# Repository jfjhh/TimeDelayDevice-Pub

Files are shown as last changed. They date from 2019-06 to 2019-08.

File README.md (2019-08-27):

Time Delay Device Documentation
===============================

See `./doc/doc-all.pdf`. It's header is reproduced below.

All of the documentation concerning the auxilliary files for the project
is assembled here. What follows is a description of the contents of each
directory.

-   `adjustable-delay`: Schematics and ideas for implementing adjustable
    delay in the circuit. The subdirectory `Linear` contains a tenative
    schematic (KiCAD files and <span
    style="font-variant:small-caps;">pdf</span>) of a circuit that
    implements the different clock frequencies by counting, while
    `Arbitrary` gives what I have so far in creating an arbitrary delay
    circuit.

-   `arduino`: The code uploaded to the Arduino Due.

-   `characterization`: Contains many different parts of the code used
    to analyze the characterization data for the device, and includes
    instructions on how to program the history.

-   `doc`: The top-level documentation directory (this one).

-   `fifo-p3f`: The KiCAD files for the device, as well as a schematic
    <span style="font-variant:small-caps;">pdf</span> and the gerber
    files that I sent for manufacture.

-   `figures`: The images and GNUPlot code used to create the figures
    for the paper.[^1]

-   `program-rescaling`: The code used to calculate the gain and offset
    resistor values to be optimal, given the constraints of E-series
    values and the overall resistances needed.

-   `triangle`: The code used to generate the spumpus (initial history
    signal) for the triangle-<span
    style="font-variant:small-caps;">dde</span> (relay-control) circuit
    in the paper. This is a good starting point if you want to program
    something different.

[^1]: *Spumpus* stands for spiky lumpus, where *lumpus* refers to a
    lumpy-looking signal. We want a strange signal for the programming
    to demonstrate that it is really *arbitrary*.

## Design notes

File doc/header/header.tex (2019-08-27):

%        File: header.tex
%     Created: Mon Aug 26 08:00 PM 2019 P
% Last Change: Mon Aug 26 08:00 PM 2019 P
%
\documentclass[11pt,letterpaper]{article}

\title{Time Delay Device Files Documentation}
\author{Alex Striff}
\date{August 26, 2019}

\begin{document}
\maketitle

All of the documentation concerning the auxilliary files for the project is
assembled here. What follows is a description of the contents of each directory.

\begin{itemize}
  \item \texttt{adjustable-delay}: Schematics and ideas for implementing
    adjustable delay in the circuit. The subdirectory \texttt{Linear} contains a
    tenative schematic (KiCAD files and \textsc{pdf}) of a circuit that
    implements the different clock frequencies by counting, while
    \texttt{Arbitrary} gives what I have so far in creating an arbitrary delay
    circuit.
  \item \texttt{arduino}: The code uploaded to the Arduino Due.
  \item \texttt{characterization}: Contains many different parts of the
    code used to analyze the characterization data for the device, and includes
    instructions on how to program the history.
  \item \texttt{doc}: The top-level documentation directory (this one).
  \item \texttt{fifo-p3f}: The KiCAD files for the device, as well as a
    schematic \textsc{pdf} and the gerber files that I sent for manufacture.
  \item \texttt{figures}: The images and GNUPlot code used to create the figures
    for the paper.\footnote{\emph{Spumpus} stands for spiky lumpus, where
      \emph{lumpus} refers to a lumpy-looking signal. We want a strange signal
    for the programming to demonstrate that it is really \emph{arbitrary}.}
  \item \texttt{program-rescaling}: The code used to calculate the gain and
    offset resistor values to be optimal, given the constraints of E-series
    values and the overall resistances needed.
  \item \texttt{triangle}: The code used to generate the spumpus (initial
    history signal) for the triangle-\textsc{dde} (relay-control) circuit in the
    paper. This is a good starting point if you want to program something
    different.
\end{itemize}

\end{document}

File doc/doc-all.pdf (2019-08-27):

# Time Delay Device Files Documentation

Alex Striff

August 26, 2019

All of the documentation concerning the auxilliary files for the project is assembled here. What follows is a description of the contents of each directory.

- adjustable-delay: Schematics and ideas for implementing adjustable delay in the circuit. The subdirectory Linear contains a tenative schematic (KiCAD files and pdf) of a circuit that implements the different clock frequencies by counting, while Arbitrary gives what I have so far in creating an arbitrary delay circuit.
- arduino: The code uploaded to the Arduino Due.
- characterization: Contains many different parts of the code used to analyze the characterization data for the device, and includes instructions on how to program the history.
- doc: The top-level documentation directory (this one).
- fifo-p3f: The KiCAD files for the device, as well as a schematic pdf and the gerber files that I sent for manufacture.
- figures: The images and GNUPlot code used to create the figures for the paper.¹
- program-rescaling: The code used to calculate the gain and offset resistor values to be optimal, given the constraints of E-series values and the overall resistances needed.
- triangle: The code used to generate the spumpus (initial history signal) for the triangle-dde (relay-control) circuit in the paper. This is a good starting point if you want to program something different.

1Spumpus stands for spiky lumpus, where lumpus refers to a lumpy-looking signal. We want a strange signal for the programming to demonstrate that it is really arbitrary.

1

# characterization

## August 26, 2019

In [1]: using StatsBase
using Statistics
using CSV
using DSP
using Measurements
using CRC
using Optim
using Tables

## 1 Delayed Signal Computations

### 1.1 DAC Rise Time

In [2]: rtdata = CSV.File("./data/Tek004.csv"; header=false) rtweights = FrequencyWeights(rtdata.Column2)
rt = mean(rtdata.Column1, rtweights)
rtσ = std(rtdata.Column1, rtweights, corrected=true)

Out[2]: 1.1492676743389036e-9

In [3]: rtσ /= 4 # For a 1 Vpp square wave edge rt /= 4

Out[3]: 1.290866506382043e-7

In [4]: (rt ± rtσ) * 1e9

Out[4]:
129.09 ± 0.29

### 1.2 Delay Error

The steps in the error plots are from single-digits on the scope, so the results should taken with a grain of salt.

In [5]: dlimit=35;
ddata = CSV.File("./delay_linearity.csv"; skipto=2, limit=dlimit, header=[:min, :max, :swords, :na, :clock, :signal, :rt]);
rtcorrection = vcat(repeat([rt], 13), zeros(dlimit-13));
minerr = 1e-3.*ddata.min .- (ddata.swords .* 20e-6) .+ 20e-6 - rtcorrection; maxerr = 1e-3.*ddata.max .- (ddata.swords .* 20e-6) - rtcorrection;

In [6]: last(ddata.swords)

Out[6]: 9000

Clock is at 50 kHz.

### 1.3 Estimated Internal Propagation Delay

Roughly estimated from risetime-corrected delay data.

In [7]: pt = mean(map(mean, [minerr[1:13], maxerr[1:13]])) ./ 1e-9 # ns

Out[7]: 40.14411859255405

### 1.4 In-Out Difference Mean

In [8]: meandata = CSV.File("./data/diffmean2.csv"; header=false); meanweights = FrequencyWeights(meandata.Column2);
diffµ = mean(meandata.Column1, meanweights);
diffµσ = std(meandata.Column1, meanweights, corrected=true); (diffµ ± diffµσ) * 1e3 # mV

Out[8]:
−1.023 ± 0.095

### 1.5 In-Out Difference ACRMS (Standard Deviation)

In [9]: acrmsdata = CSV.File("./data/diffacrms2.csv"; header=false); acrmsweights = FrequencyWeights(acrmsdata.Column2);
diffσ = mean(acrmsdata.Column1, acrmsweights);
diffσσ = std(acrmsdata.Column1, acrmsweights, corrected=true); (diffσ ± diffσσ) * 1e3 # mV (RMS)

Out[9]:
1.035 ± 0.058

## 2 Output Plots

- Input: 50 Hz sine wave.
- Clock: 50 kHz.
- Delay: 1000 swords.
- Measurement Bandwidth: 100 MHz.

Ignore the naming of the file. The signal is actually at 50 Hz.

In [10]: diff500 = CSV.File("./data/500HzDiff100MHz.csv", skipto=10, header=[:t, :v])

Out[10]: CSV.File("./data/500HzDiff100MHz.csv"): Size: 1250000 x 2
Tables.Schema:
:t | Float64
:v | Float64

In [11]: # Resample/decimate for faster processing #ddiff500t = resample(diff500.t, 1 // 10); #ddiff500v = resample(diff500.v, 1 // 10);

ddiff500t = diff500.t;
ddiff500v = diff500.v;
- Input: 5 kHz sine wave.
- Clock: 5 MHz.
- Delay: 1000 swords.
- Measurement Bandwidth: 250 MHz.

Ignore the naming of the file. The signal is actually at 5 kHz.

In [12]: diff5M = CSV.File("./data/5MHzDiff250MHz.csv", skipto=10, header=[:t, :v])

Out[12]: CSV.File("./data/5MHzDiff250MHz.csv"):
Size: 625000 x 2
Tables.Schema:
:t | Float64
:v | Float64

In [13]: # Resample/decimate for faster processing #ddiff5Mt = resample(diff5M.t, 1 // 10); #ddiff5Mv = resample(diff5M.v, 1 // 10);

ddiff5Mt = diff5M.t;
ddiff5Mv = diff5M.v;

## 3 Initial History Programming

In [14]: little_endian(x) = UInt8.([x & 0x00FF, x >> 8]);

In [15]: prog_words = [
| 0x0000, 0x07FF, 0x0FFF, 0x07FF,
| 0x0000, 0x07FF, 0x0FFF, 0x07FF,
| 0x0000, 0x07FF, 0x0FFF, 0x07FF,
| 0x0000, 0x07FF, 0x0FFF, 0x07FF
];
waveform_file = "./prog_debug.bin"; write(waveform_file, prog_words);
crc32 = crc(CRC_32);
prog_crc = crc32(vcat(little_endian.(prog_words)...)); display(prog_crc);

0x7a569719

### 3.1 Initial History Programming Instructions

- Open Realterm.
- On the Display tab, check the newLine mode box.
- On the Port tab, set the Baud rate to 115200.
- Select the Port that the Arduino Due is plugged in to, such as 6 = \USBSER000.
- Press enter in the Port field to open the port. You should see text from the Arduino Due.
- On the Send tab, select the first text field.
- Type ph N, where N is the number of words that you want to program.

### - Click the Send ASCII button. (Do not include a line feed in this command, as it will be

interpreted as data).
- In the Dump File to Port section, click the ellipses (...) box.
- Select the history data file that you want to program.
- Under Delays, set the first entry (Character Delay) to 1.
- Click Send File. You should see a hexdump of the data from the Arduino Due as it is trans-mitted.
- At the end of the transmission, there will be a line that says CRC: 0x.... Check that this matches the CRC_32 of the sent data (little-endian).
- Send the go command to the Arduino Due to switch to the external input and clocks.

## 4 Filtered Output Plots

### 4.1 Signal A

- Input: 5 kHz sine wave.
- Clock: 5 MHz.
- Delay: 1000 swords.
- Measurement Bandwidth: 250 MHz.

In [16]: ain = CSV.File("./data/5-5-in.csv", skipto=10, header=[:t, :v]); # Input signal aout = CSV.File("./data/5-5-unfiltered.csv",
skipto=10, header=[:t, :v]); # Unfiltered output
arc = CSV.File("./data/5-5-106kHz-RC.csv",
skipto=10, header=[:t, :v]); # 106 kHz RC filter (single-pole) abessel4 = CSV.File("./data/5-5-bessel4.csv",
skipto=10, header=[:t, :v]); # ~121 kHz Bessel filter (four-pole)

In [17]: abessel4vpp = maximum(abessel4.v) - minimum(abessel4.v);

### 4.2 Signal B

- Input: 20 kHz symmetric triangle wave.
- Clock: 5 MHz.
- Delay: 1000 swords.

- Measurement Bandwidth: 250 MHz.

In [18]: bin = CSV.File("./data/5-20-in.csv", skipto=10, header=[:t, :v]); # Input signal. ZI: 6249.5 bout = CSV.File("./data/5-20-unfiltered.csv",
skipto=10, header=[:t, :v]); # Unfiltered output
brc = CSV.File("./data/5-20-RC.csv",
skipto=10, header=[:t, :v]); # 106 kHz RC filter (single-pole)
bbessel4 = CSV.File("./data/5-20-bessel4.csv",
skipto=10, header=[:t, :v]); # ~121 kHz Bessel filter (4-pole). ZI: -0.5

In [19]: bbessel4vpp = maximum(bbessel4.v) - minimum(bbessel4.v);

### 4.3 Nelder-Mead Optimization of Filter Output Gain and Phase

In [20]: s∆t = 3.2e-10;

span = 0.5;
margin = (1 - span) / 2;
function slidesamples(x, n, m)
xlen = length(x);
a = mod(Int64(floor(n)), xlen);
b = mod(Int64(floor(n) + floor(m)), xlen);
x[a:b]
end
stdslide(x; m=margin) = slidesamples(x, m*length(x), span*length(x)); function modifywave(y, n, k, off)
off .+ (k .* slidesamples(y, n * length(y), span*length(y))) end
function waveerr(x, y, s)
xlen = length(x);
rms(stdslide(x) .- modifywave(y, s...)) end

Out[20]: waveerr (generic function with 1 method)

The default algorithm that optimize will use here is Nelder-Mead.

In [21]: arcoptim = optimize(s -> waveerr(ain.v, arc.v, s), [margin, 1., 0.]);

In [22]: abessel4optim = optimize(s -> waveerr(ain.v, abessel4.v, s), [margin, 1.0 / abessel4vpp, 0.]);

In [23]: arco = modifywave(arc.v, arcoptim.minimizer...);

In [24]: abessel4o = modifywave(abessel4.v, abessel4optim.minimizer...);

In [25]: CSV.write("paout.csv",
(aint=stdslide(ain.t) .* 1e6, ainv=stdslide(ain.v) .* 1e3, aoutt=stdslide(aout.t) .* 1e6,
aoutv=stdslide(aout.v) .* 1e3,
abessel4t=stdslide(abessel4.t) .* 1e6, abessel4v=stdslide(abessel4.v) .* 1e3 * abessel4optim.minimizer[2]))

Out[25]: "paout.csv"

In [26]: arcodiff = stdslide(ain.v) .- arco; abessel4odiff = stdslide(ain.v) .- abessel4o;

In [27]: abessel4odiffµ = mean(abessel4odiff)

Out[27]: -7.533094976133311e-6

In [28]: abessel4odiffσ = std(abessel4odiff)

Out[28]: 0.0029591421680602945

# Triangle History Generation

## August 26, 2019

In [1]: using CRC
using Plots

gr()

Out[1]: Plots.GRBackend()

In [2]: f = 6e6;
τ = 1e-3;
n = τ*f;

The last two words will be replaced with a value close to 0V (0x0800) when programmed, since we cannot program the initial DAC output.

In [3]: g(t) = -0.45 * (0.9 * sin(t * 2.5*3π / 2) * atan(8π * t)
- 0.1 * abs(atan(sec(t * 20π))) - 0.5 * abs(atan(cot(t * 5π))) + 0.02 * cos(100π * t)) - 0.4;
ts = (0:n-1) / (n-1);
gs = g.(ts);
plot(ts, gs, xlim=(0, 1),
xlabel = "Nondimensionalized delay time", ylabel = "Nondimensionalized amplitude (±1)", label = "History Signal", legend=:topleft)

Out[3]:

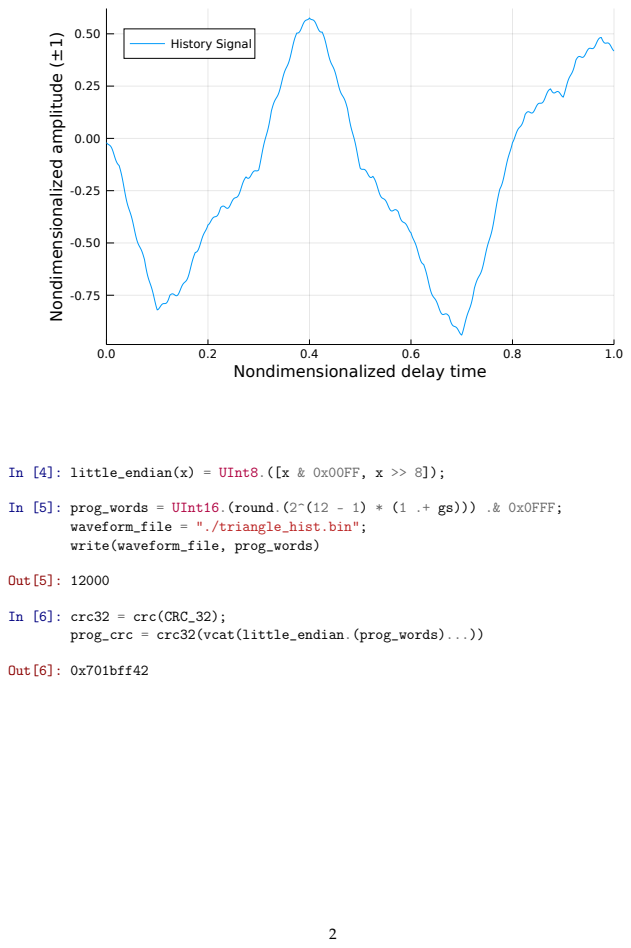
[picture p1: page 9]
In [4]: little_endian(x) = UInt8.([x & 0x00FF, x >> 8]);; waveform_file = "./triangle_hist.bin";; write(waveform_file, prog_words); Out[5]: 12000; In [6]: crc32 = crc(CRC_32);; prog_crc = crc32(vcat(little_endian.(prog_words)...)); Out[6]: 0x701bff42

Nondimensionalized amplitude (±1) History Signal

Nondimensionalized delay time

In [5]: prog_words = UInt16.(round.(2^(12 - 1) * (1 .+ gs))) .& 0x0FFF;

# program-rescaling

## August 26, 2019

## 1 Offset and gain calculations for Due DAC to ADC opamps

### 1.1 Voltages that determine required offset and gain

In [1]: V_DL | = 3.3 * 1/6; # V. Due DAC0 minimum voltage
V_DH | = 3.3 * 5/6; # V. Due DAC0 maximum voltage
V_AL | = -2.5; | # V. ADC input minimum voltage
V_AH | = 2.5; | # V. ADC input maximum voltage
offset = ((V_AH + V_AL) - (V_DH + V_DL)) / 2.; # V gain = (V_AH - V_AL) / (V_DH - V_DL); # V/V println("Offset:\t", offset, " V\nGain:\t", gain, " V");
Offset: | -1.65 V
Gain: | 2.2727272727272725 V

### 1.2 Choice of resistor tolerance range (the E-series to use)

In [2]: E3 = [1.0, 2.2, 4.7]; # Very common
E24 = [
| 1.0, 1.1, 1.2, 1.3, 1.5, 1.6, 1.8, 2.0, 2.2, 2.4, 2.7, 3.0, 3.3, 3.6, 3.9, 4.3, 4.7, 5.1, 5.6, 6.2, 6.8, 7.5, 8.2, 9.1

]; # 5% tolerance

In [3]: E_series = E24;

Evaluates f on all possible combinations of resistors in a given E-series.

In [4]: function combinations(E, f)
| span = 1:length(E)
[[f(E[i], E[j]), E[i], E[j]]
| for i in span for j in span] # [[f(x, y), x, y]]
end

Out[4]: combinations (generic function with 1 method)

Finds the nearest E-series value to the value given.

In [5]: function nearest(E, x)
p = floor(log10(x));
y = x / 10^p;
best = first(sort(E, lt = (a, b) -> abs(y - a) < abs(y - b))); best * 10^p;
end

Out[5]: nearest (generic function with 1 method)

### 1.3 Offset component selection calculations

### Improved calculation of the output voltage of the LM4041-ADJ where Vref depends upon VO

(V_Onom here).

In [6]: V_Onom = abs(offset); # V
V_Y = 1.240; # V
∆V_O = V_Onom - V_Y; # V
∆V_ref_∆V_O = -1.55e-3; # V/V. Absolute worst case: -3 mV/V V_ref = V_Y + ∆V_O * ∆V_ref_∆V_O; # V
R2_to_R1 = (V_Onom / V_ref) - 1.; # Ω/Ω

VO(ratio) = V_ref * (ratio + 1.);
println("V_ref = ", V_ref, " V");

V_ref = 1.2393645 V

Selection parameters.

In [7]: ratio_tolerance = 1.; # % RV_off = 1.0e3; # Ω
println("We want a resistor ratio of ", R2_to_R1, " Ω/Ω and ",

ratio_tolerance, "% nominal tolerance.");

We want a resistor ratio of 0.33132746661696366 Ω/Ω and 1.0% nominal tolerance.

Calculate the best resistors to choose to give the best nominal ratio.

In [8]: offset_ratio(x, y, off) = (x + 0.5 * off) / (y + 0.5 * off); # Divide RV_off by 1e3 so that it is at the same scale as the E-series values.
off_ratios | = combinations(E_series,
# [[Ω/Ω, Ω, Ω]]. [[ratio, R2, R1]]

(x, y) -> offset_ratio(x, y, RV_off / 1e3));
off_ratios_tol = filter(x -> ratio_tolerance / 100. > abs(1. - x[1] / R2_to_R1), off_ratios); # [[Ω/Ω, Ω, Ω]]

off_ratios_s = sort(off_ratios_tol, lt = (x, y) -> isless(abs(x[1] - R2_to_R1), abs(y[1] - R2_to_R1))); # [[Ω/Ω, Ω, Ω]]

if (length(off_ratios_s) > 0)
R1 = off_ratios_s[1][3] * 1e3; # Ω
R2 = off_ratios_s[1][2] * 1e3; # Ω

display(off_ratios_s);
println("Best offset resistor values:\n", "R2: ", R2 / 1e3, " kΩ\n",
"R1: ", R1 / 1e3, " kΩ");

else
println("No combinations give a ", ratio_tolerance, "% offset tolerance."); end

3-element Array{Array{Float64,1},1}: [0.333333, 1.1, 4.3]
[0.333333, 2.4, 8.2]
[0.333333, 2.7, 9.1]

Best offset resistor values: R2: 1.1 kΩ
R1: 4.3 kΩ

Calculate the margins of adjustability when a potentiometer is inserted between the two resistors.

In [9]: VO_simple(ratio) = 1.233 * (ratio + 1.);

In [10]: ratio_min = R2 / (R1 + RV_off); ratio_max = (R2 + RV_off) / R1; println("Low:\t", VO(ratio_min), " V"); println("High:\t", VO(ratio_max), " V");
println("S Low:\t", VO_simple(ratio_min), " V");
println("S High:\t", VO_simple(ratio_max), " V");
V_O_low | = VO(ratio_min) - V_Onom; # V. Negative margin away from V_Onom
V_O_high | = VO(ratio_max) - V_Onom; # V. Positive margin away from V_Onom
V_O_total = V_O_high - V_O_low; | # V. Total argin away from V_Onom
println("Offset margins **after amplification** for a ",
RV_off / 1e3, " kΩ potentiometer:\n",
"Low margin:\t", | V_O_low | * 1e3 * gain," mV\t(",
100. * V_O_low | / V_Onom, "%)\n",
"High margin:\t", | V_O_high | * 1e3 * gain, " mV\t(",
100. * V_O_high | / V_Onom, "%)\n",
"Total margin:\t", V_O_total * 1e3 * gain, " mV\t(",
100. * V_O_total / V_Onom, "%)");
Low: | 1.4965910943396226 V
High: | 1.844635534883721 V
S Low: | 1.4889056603773585 V
S High: | 1.8351627906976746 V

Offset margins **after amplification** for a 1.0 kΩ potentiometer:

Low margin: | -348.65660377358483 mV | (-9.297509433962265%)
High margin: | 442.3534883720931 mV | (11.796093023255818%)
Total margin: | 791.010092145678 mV | (21.093602457218083%)

### 1.3.1 LM4041-ADJ resistor selection

In [11]: Vcc_ref = 5.; # V V_R_ref = Vcc_ref - V_Onom; # V R_load = R1 + RV_off + R2; # Ω

I_load = V_Onom / R_load; # A
I_Q = 2.9e-3; # A
I_t = I_Q + I_load;
R_ref = nearest(E_series, V_R_ref / I_t); # Ω

I_ref = V_R_ref / R_ref; # A
println("Best resistor for the LM4041-ADJ (I_load = ", I_load * 1e3, " mA):\n", "R_ref:\t", R_ref / 1e3, " kΩ\n",

"I_ref:\t", I_ref * 1e3, " mA\t(", 100. * (I_ref - I_t) / I_t, "%)\n", "Power:\t", V_R_ref * I_ref * 1e3, " mW");

Best resistor for the LM4041-ADJ (I_load = 0.2578125 mA):
R_ref: | 1.1 kΩ
I_ref: | 3.045454545454546 mA | (-3.558094552651698%)
Power: | 10.202272727272728 mW

### 1.4 Gain component selection calculations

Selection parameters.

In [12]: div_tolerance = 1.; # % RV_gain = 1.0e3 # Ω

#div_nom = 1. / gain;

div_nom = 5.0 / 2.2;
println("We want a resistor divider with a gain of ", div_nom, " V/V and ", div_tolerance, "% nominal tolerance.");

We want a resistor divider with a gain of 2.2727272727272725 V/V and 1.0% nominal tolerance.

Calculate the best resistors to choose to give the best nominal resistor divider.

In [13]: # For noninverting gain configuration
offset_divider(x, y, off) = 1. + (y + 0.5 * off) / (x + 0.5 * off);
# Divide RV_gain by 1e3 so that it is at the same scale as the E-series values. gain_divs = combinations(E_series, # [[Ω/Ω, Ω, Ω]]. [[ratio, Rb, Ra]]

(x, y) -> offset_divider(x, y, RV_gain / 1e3));
gain_divs_tol = filter(x -> div_tolerance / 100. > abs(1. - x[1] / div_nom), gain_divs); # [[Ω/Ω, Ω, Ω]]
gain_divs_s = sort(gain_divs_tol, # [[Ω/Ω, Ω, Ω]]

lt = (x, y) -> isless(abs(x[1] - div_nom), abs(y[1] - div_nom))); if (length(gain_divs_s) > 0)
Ra = gain_divs_s[1][3] * 1e3; # Ω
Rb = gain_divs_s[1][2] * 1e3; # Ω

display(gain_divs_s);
println("Best gain resistor values:\n", "Ra: ", Ra / 1e3, " kΩ\n",
"Rb: ", Rb / 1e3, " kΩ");

else
println("No combinations give a ", div_tolerance, "% gain tolerance."); end

13-element Array{Array{Float64,1},1}: [2.27273, 3.9, 5.1]
[2.27083, 4.3, 5.6]
[2.26829, 3.6, 4.7]
[2.27778, 1.3, 1.8]
[2.28, 2.0, 2.7]
[2.28125, 2.7, 3.6]
[2.26316, 3.3, 4.3]
[2.26087, 1.8, 2.4]
[2.28571, 1.6, 2.2]
[2.25714, 3.0, 3.9]
[2.28846, 4.7, 6.2]
[2.25, 1.1, 1.5]
[2.25, 1.5, 2.0]

Best gain resistor values: Ra: 5.1 kΩ
Rb: 3.9 kΩ

Calculate the margins of adjustability when a potentiometer is inserted between the two resistors.

In [14]: div_min | = Rb / (Ra + Rb + RV_gain);
div_max | = (Rb + RV_gain) / (Ra + Rb + RV_gain);
div_low | = div_min | - div_nom; # V. Negative margin away from V_Onom
div_high | = div_max | - div_nom; # V. Positive margin away from V_Onom
div_total = div_high - div_low; # V. Total margin away from V_Onom println("Gain margins for a ", RV_gain / 1e3, " kΩ potentiometer:\n",
"Low margin:\t", | div_low | * 1e3, " mV\t(",
100. * div_low | / div_nom, "%)\n",
"High margin:\t", | div_high | * 1e3, " mV\t(",
100. * div_high | / div_nom, "%)\n",

"Total margin:\t", div_total * 1e3, " mV\t(",
100. * div_total / div_nom, "%)");

Gain margins for a 1.0 kΩ potentiometer:

Low margin: | -1882.7272727272723 mV | (-82.83999999999999%)
High margin: | -1782.7272727272725 mV | (-78.44%)
Total margin: | 99.99999999999987 mV | (4.399999999999994%)

# Delay Plot GNUPlot Output and Code

## Alex Striff

## August 26, 2018

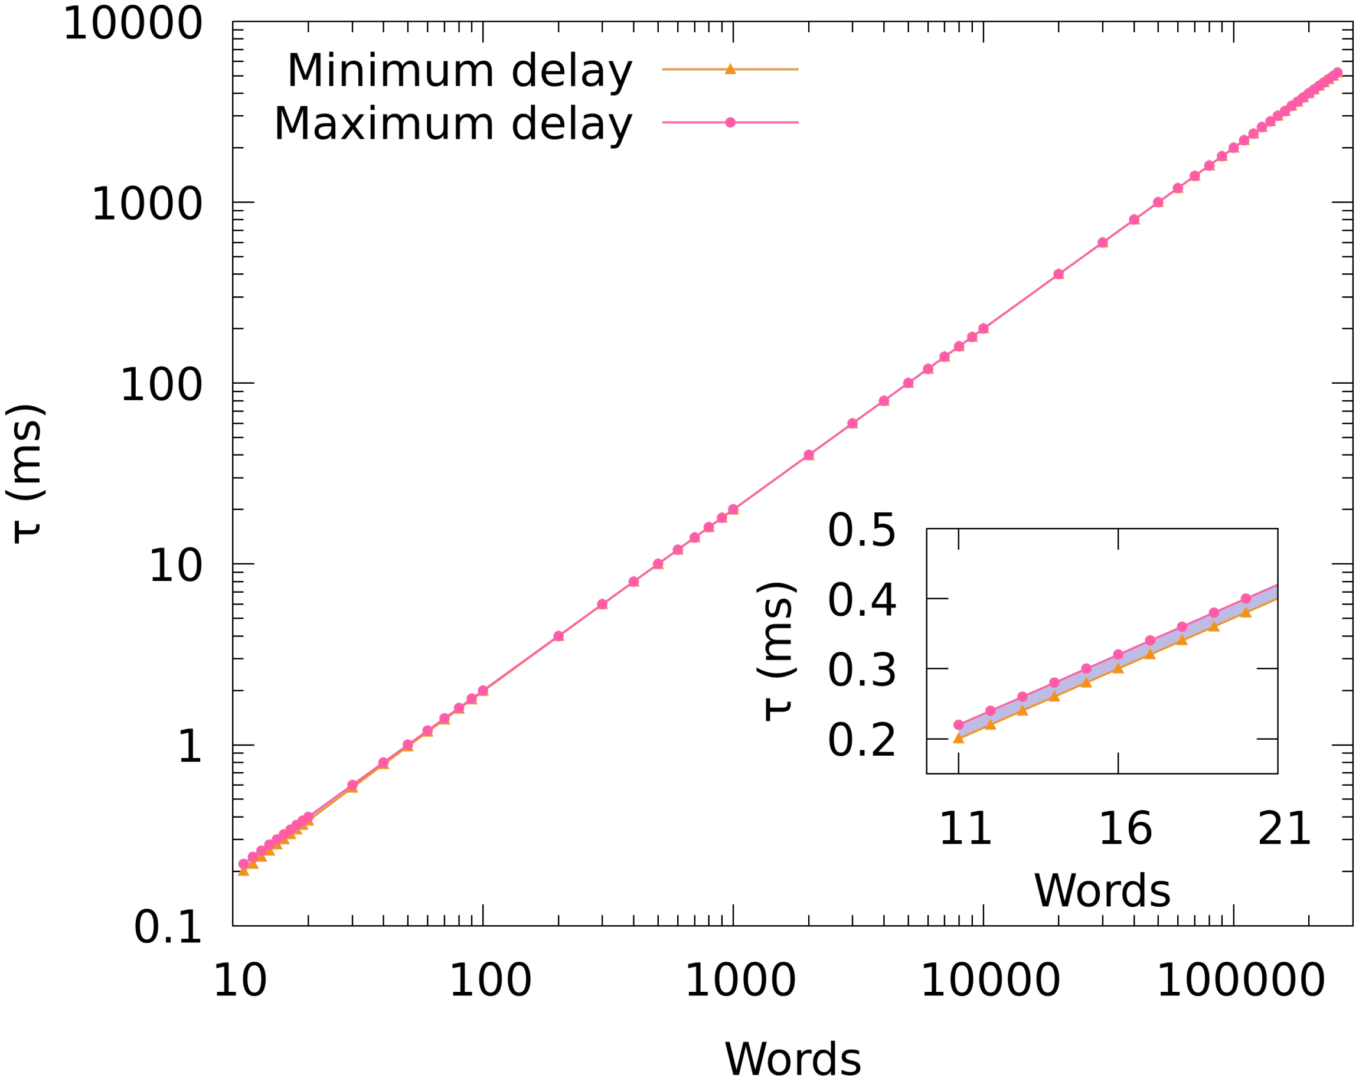
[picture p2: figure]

Figure 1: Paper, color version.

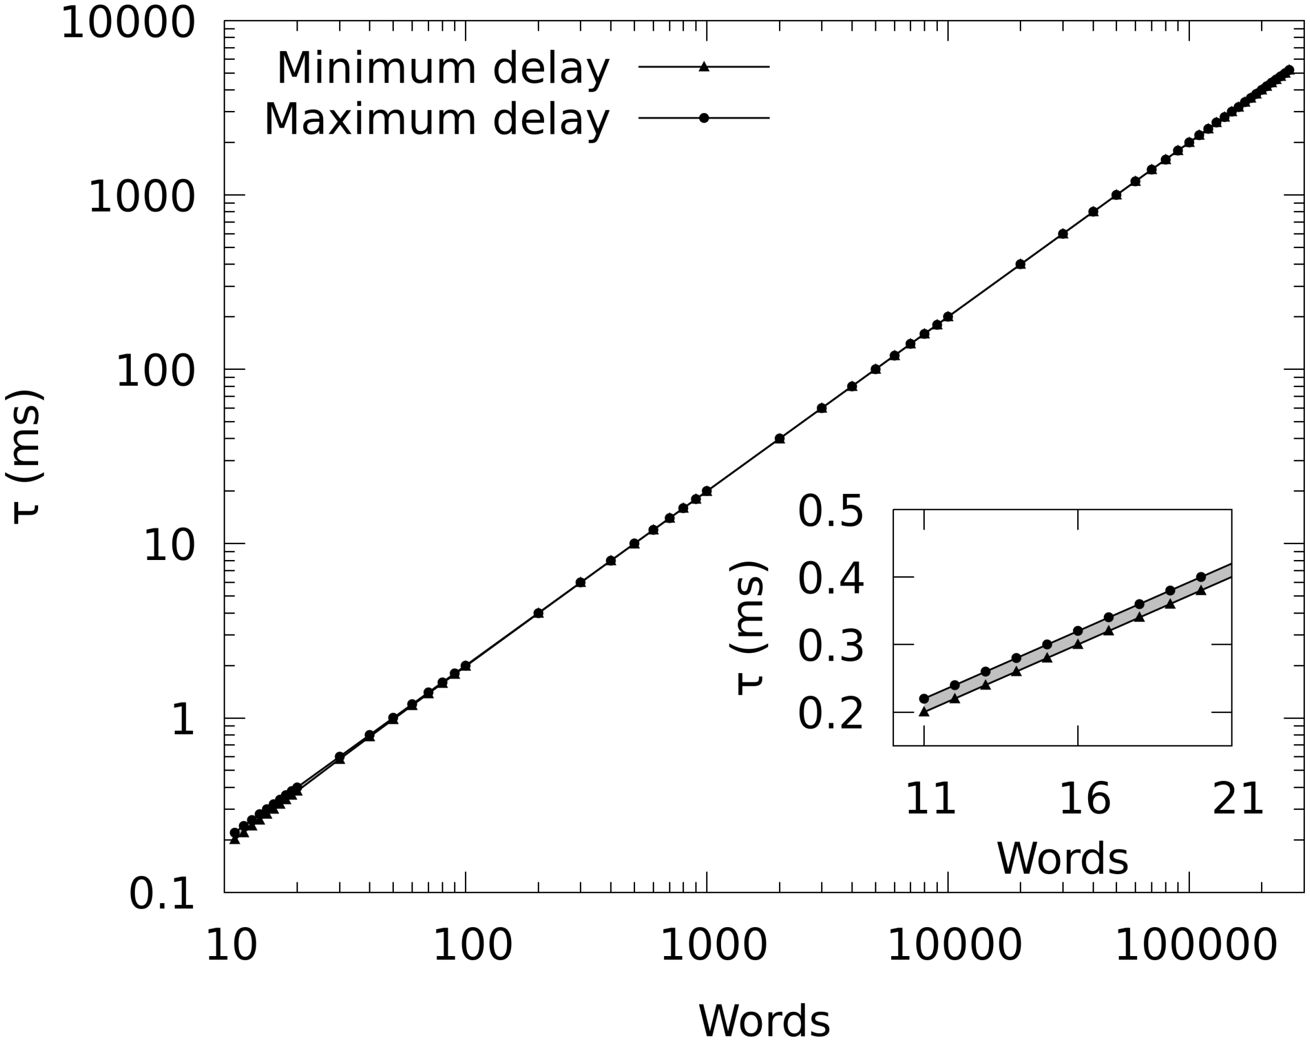
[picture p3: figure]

Figure 2: Paper, grayscale version.

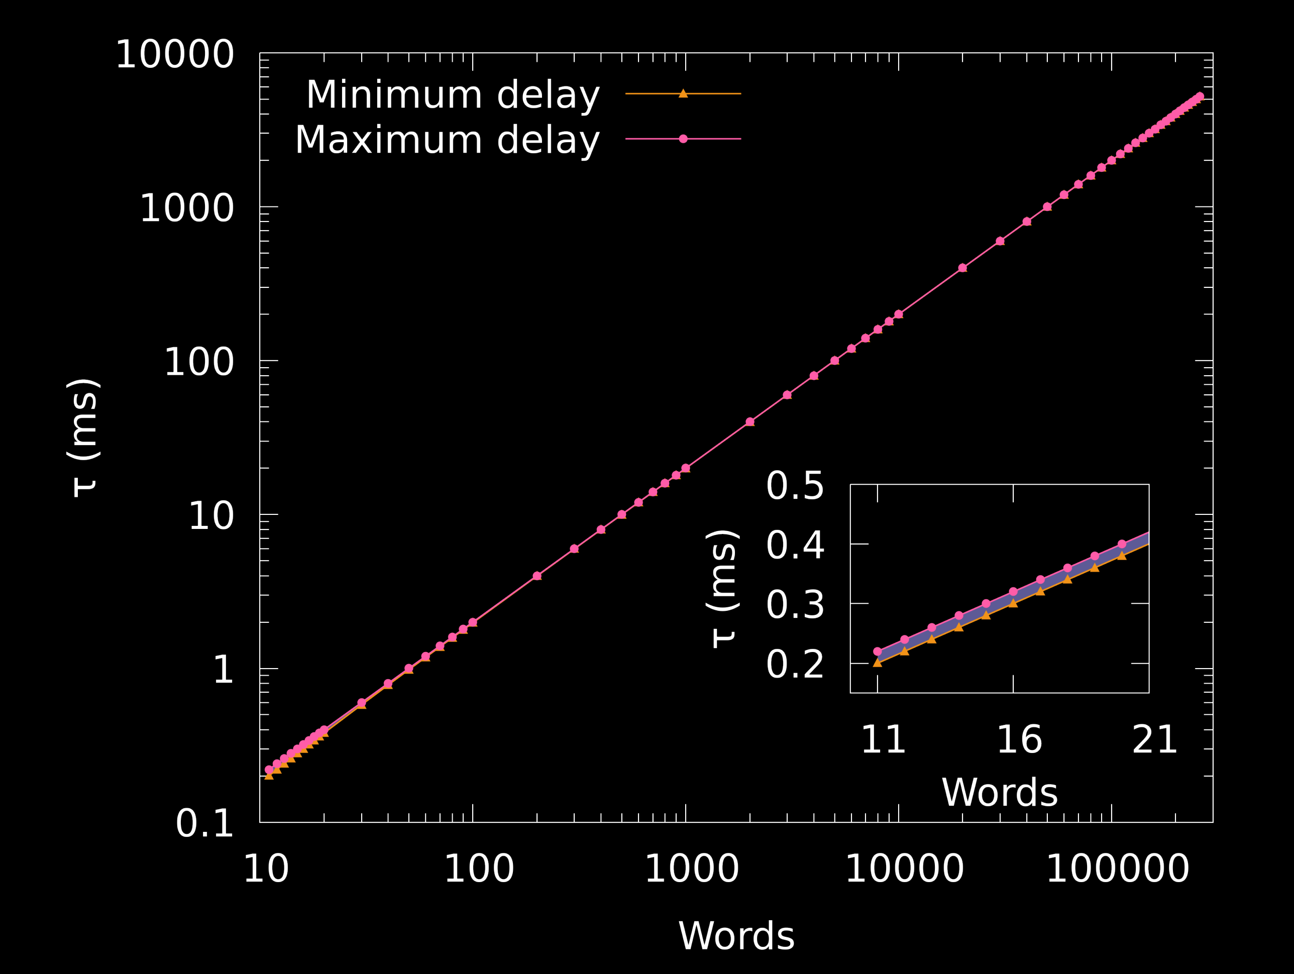
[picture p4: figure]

Figure 3: Dark Owl version (beamer slides).

set terminal pngcairo transparent enhanced font "Droid Sans,72" \ fontscale 1.0 size 3200, 2400

# Dark Owl

text = '#ffffff'
shade = '#5d5a96' # (rgb(OwlRed) .+ rgb(OwlBlue)) .* 3/8 mindelay = '#f29318' # OwlYellow
maxdelay = '#ff5ca8' # OwlRed
set output 'delayplot-do.png'

# Paper Color

# text = '#000000'

# shade = '#bfbce4' # 0.25*OwlRed + 0.25*OwlBlue + 0.5*white # mindelay = '#f29318' # OwlYellow

# maxdelay = '#ff5ca8' # OwlRed

# set output 'delayplot-pc.png'

# Paper Grayscale

# text = '#000000'

# shade = '#c0c0c0'

# mindelay = '#000000'

# maxdelay = '#000000'

# set output 'delayplot-pg.png'

set multiplot
set style increment default

set border lw 3 lc rgb text set key tc rgb text
set xlabel tc rgb text
set ylabel tc rgb text

set datafile separator ',' dlin = 'delayplot.csv'

set origin 0,0
set size 1,1
set xtics auto
set key left top autotitle columnhead set xlabel 'Words'
set ylabel ' (ms)' offset 1.5,0
set logscale xy

plot [10:3e5][] \
dlin u 3:2:1 w filledcurves lt rgb shade t '', \
dlin u 3:1 w linespoints pt 9 ps 3 lw 4 lc rgb mindelay t '', \
dlin u 3:2 w linespoints pt 7 ps 3 lw 4 lc rgb maxdelay t '', \
NaN w linespoints pt 9 ps 3 lw 4 lc rgb mindelay t 'Minimum delay', \ NaN w linespoints pt 7 ps 3 lw 4 lc rgb maxdelay t 'Maximum delay'

set origin 0.5,0.15
set size 0.45,0.4
set xtics 11, 5
set ytics 0.1
unset key
set xlabel 'Words' offset 0,0.325 set ylabel ' (ms)' offset 1.5,0 unset logscale

plot [10:21][0.15:0.5] \
dlin u 3:2:1 w filledcurves lc rgb shade, \
dlin u 3:1 w linespoints pt 9 ps 3 lw 4 lc rgb mindelay, \ dlin u 3:2 w linespoints pt 7 ps 3 lw 4 lc rgb maxdelay

unset multiplot

# Difference Plot GNUPlot Output and Code

## Alex Striff

## August 26, 2018

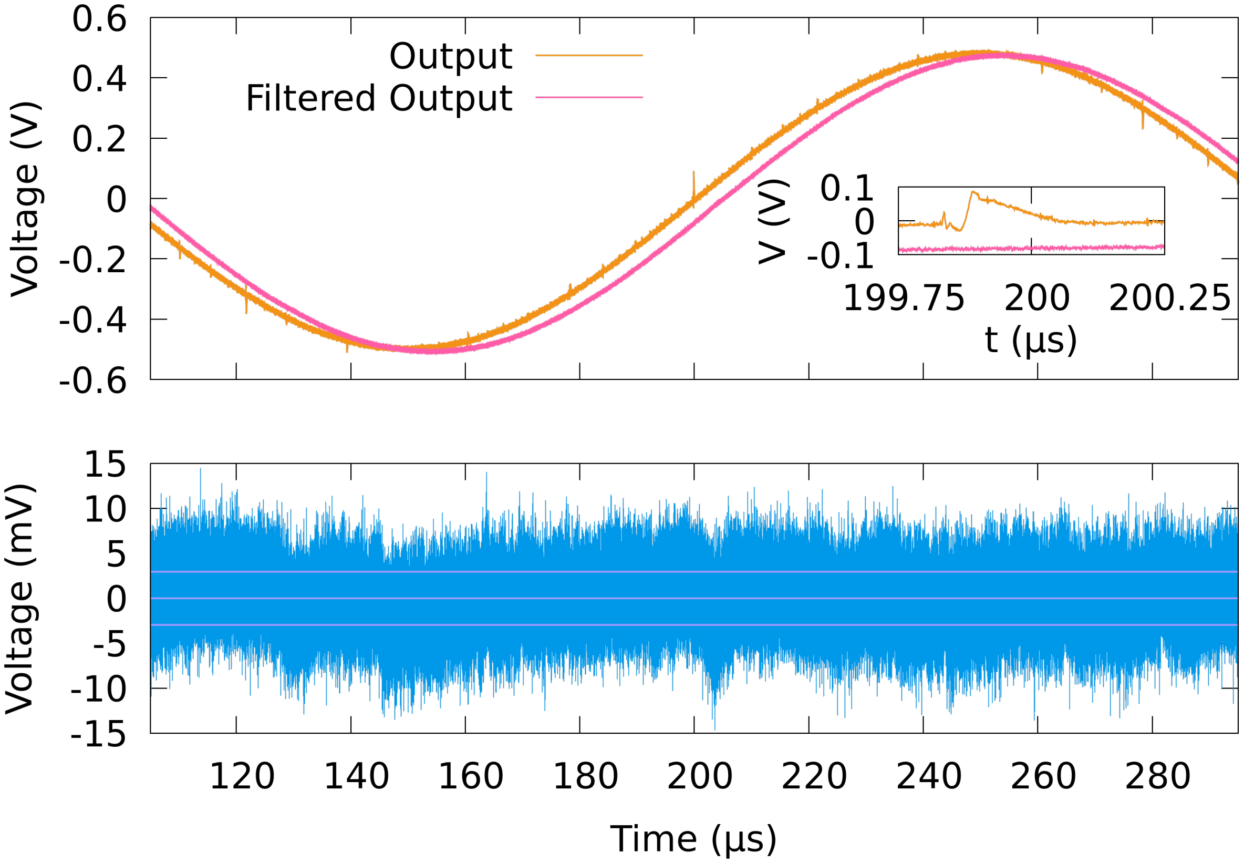
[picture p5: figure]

Figure 1: Paper, color version.

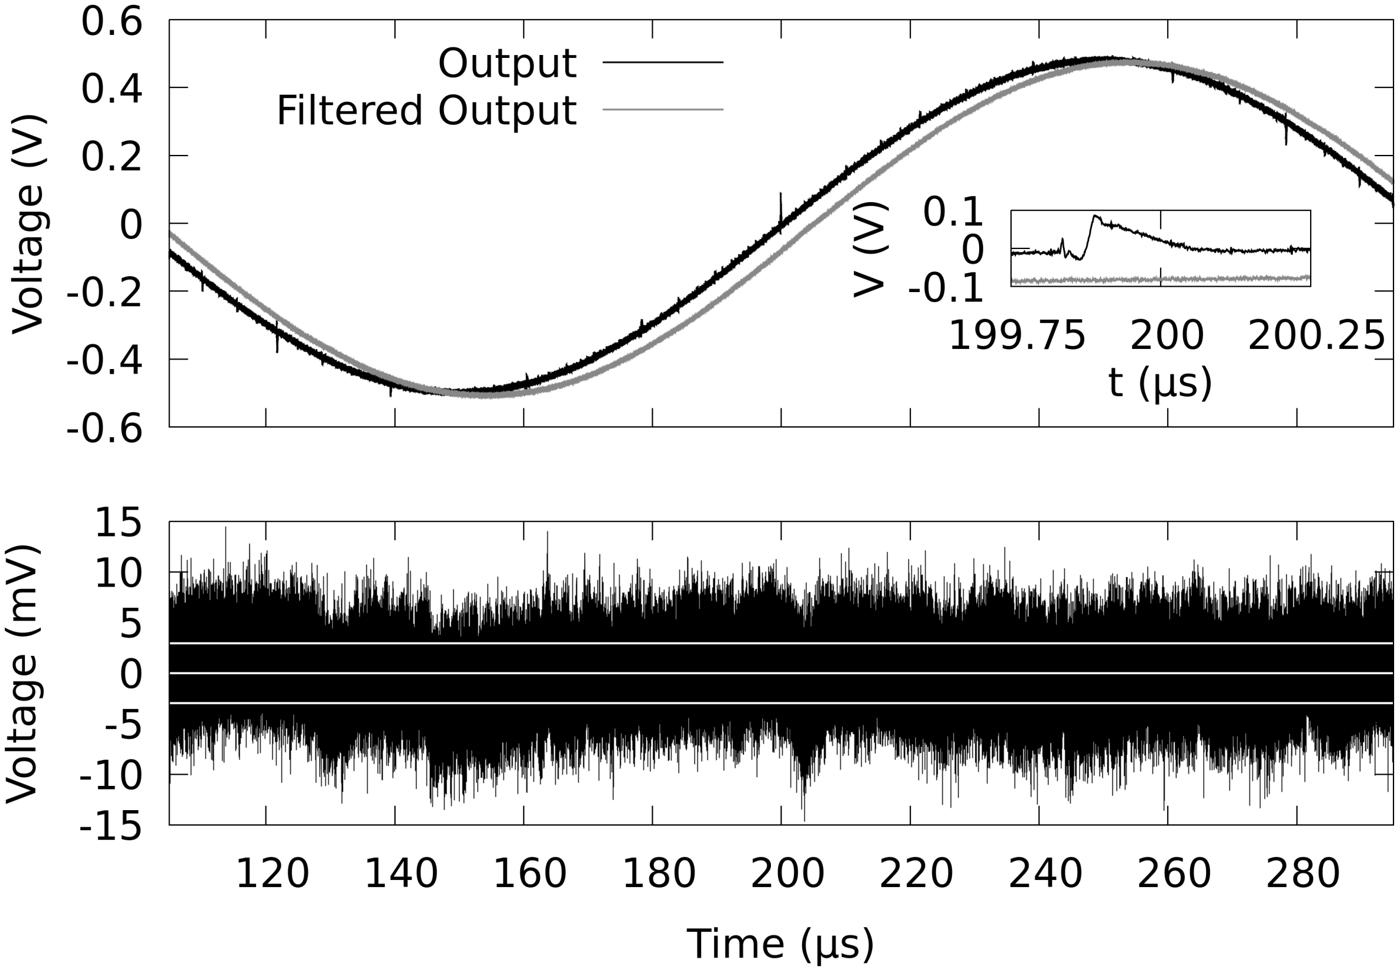
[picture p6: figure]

Figure 2: Paper, grayscale version.

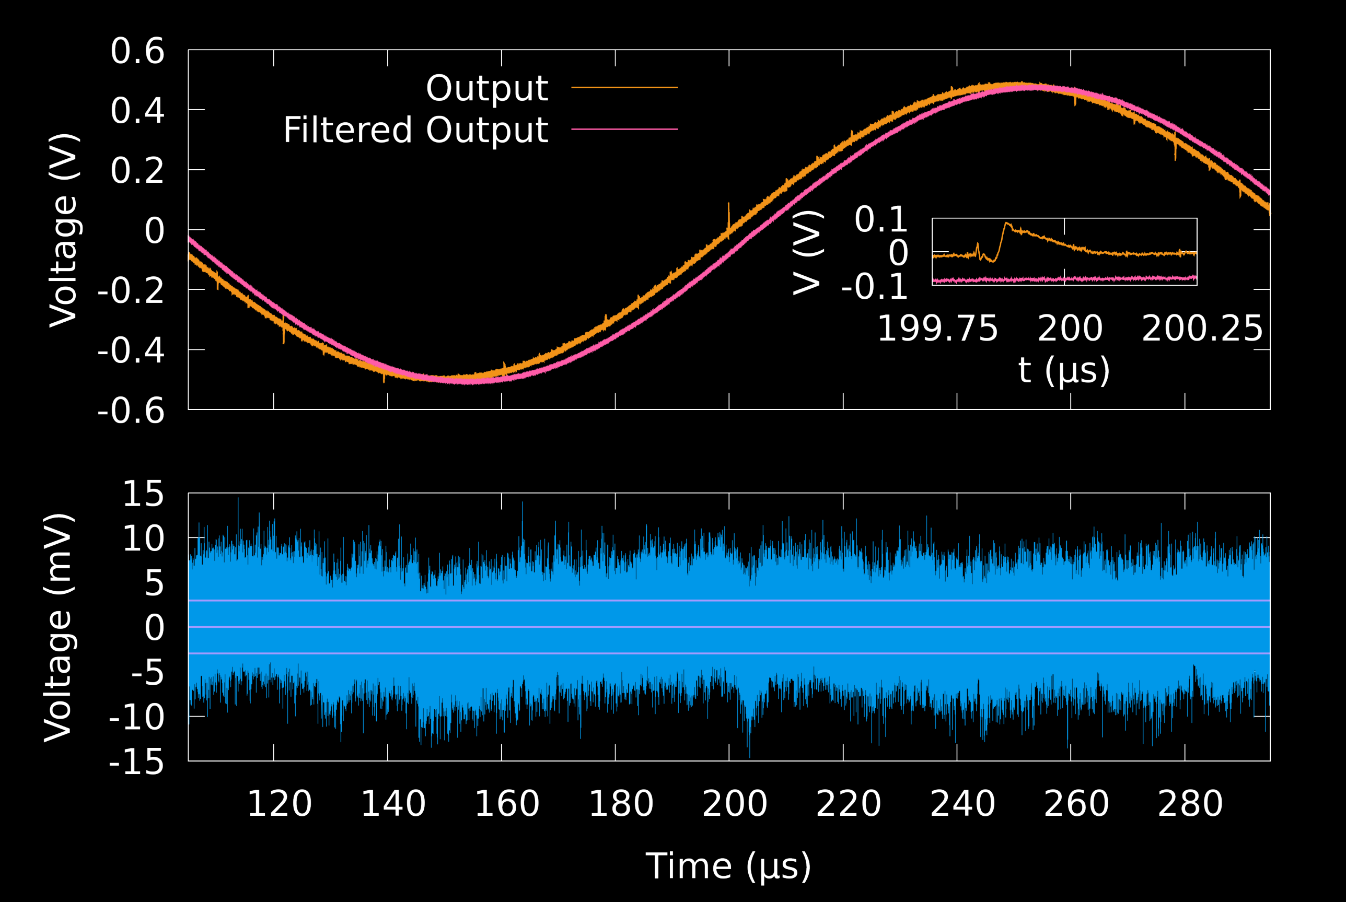
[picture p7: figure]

Figure 3: Dark Owl version (beamer slides).

set terminal pngcairo transparent enhanced font "Droid Sans,72" \ fontscale 1.0 size 3600, 2400

# Dark Owl

# text | = '#ffffff'

# aout | = '#f29318' # OwlYellow

# abessel4 = '#ff5ca8' # OwlRed

# adiff | = '#0098e9' # OwlBlue

# horiz | = '#a29bff' # (rgb(OwlRed) .+ rgb(OwlBlue)) norm. to max. blue

# set output 'diffplot-do.png'

# Paper Color

text | = '#000000'
aout | = '#f29318' # OwlYellow
abessel4 = '#ff5ca8' # OwlRed
adiff | = '#0098e9' # OwlBlue
horiz | = '#a29bff' # (rgb(OwlRed) .+ rgb(OwlBlue)) norm. to max. blue
set output 'diffplot-pc.png'

# Paper Grayscale

# text | = '#000000'

# aout | = '#000000'

# abessel4 = '#888888'

# adiff | = '#000000'

# horiz | = '#ffffff'

# set output 'diffplot-pg.png'

set border lw 3 lc rgb text set key tc rgb text
set xlabel tc rgb text
set ylabel tc rgb text

set multiplot
set style increment default

set datafile separator ',' paout = 'paout.csv'
padiff = 'padiff.csv'

# Difference

set size 1, 0.5
set origin 0, 0
set lmargin 8
set xtics auto
unset key
set xlabel 'Time (s)'
set ylabel 'Voltage (mV)'
set xrange [105:295] noreverse writeback
# set xrange [199:201] noreverse writeback # Faster to plot for debugging

plot \
padiff u 1:2 w lines lw 2 lt rgb adiff, \ padiff u 1:3 w lines lw 5 lt rgb horiz, \ padiff u 1:($3 + $4) w lines lw 5 lt rgb horiz, \ padiff u 1:($3 - $4) w lines lw 5 lt rgb horiz

# Waveforms zoom-in

set size 0.25, 0.25
set origin 0.695, 0.56
set lmargin 0
set xtics auto 0.25
set ytics auto 0.1
unset key
set xlabel 't (s)' offset 0,0.5
set ylabel 'V (V)' offset 1.25,0
set xrange [199.75:200.25] noreverse writeback

plot \
paout u 3:($4 * 1e-3) w lines lw 4 lt rgb aout t '', \

paout u 5:($6 * 1e-3) w lines lw 4 lt rgb abessel4 t ''

# Waveforms

set size 1, 0.5
set origin 0, 0.5
set lmargin 8
set xtics auto format ''
set ytics auto
unset xlabel
set key left top autotitle columnhead
set ylabel 'Voltage (V)'
set xrange [105:295] noreverse writeback
# set xrange [199:201] noreverse writeback # Faster to plot for debugging

plot \
paout u 3:($4 * 1e-3) w lines lw 4 lt rgb aout t 'Output', \
paout u 5:($6 * 1e-3) w lines lw 4 lt rgb abessel4 t 'Filtered Output'

unset multiplot

# Triangle/Spumpus Plot GNUPlot Output and Code

## Alex Striff

## August 26, 2018

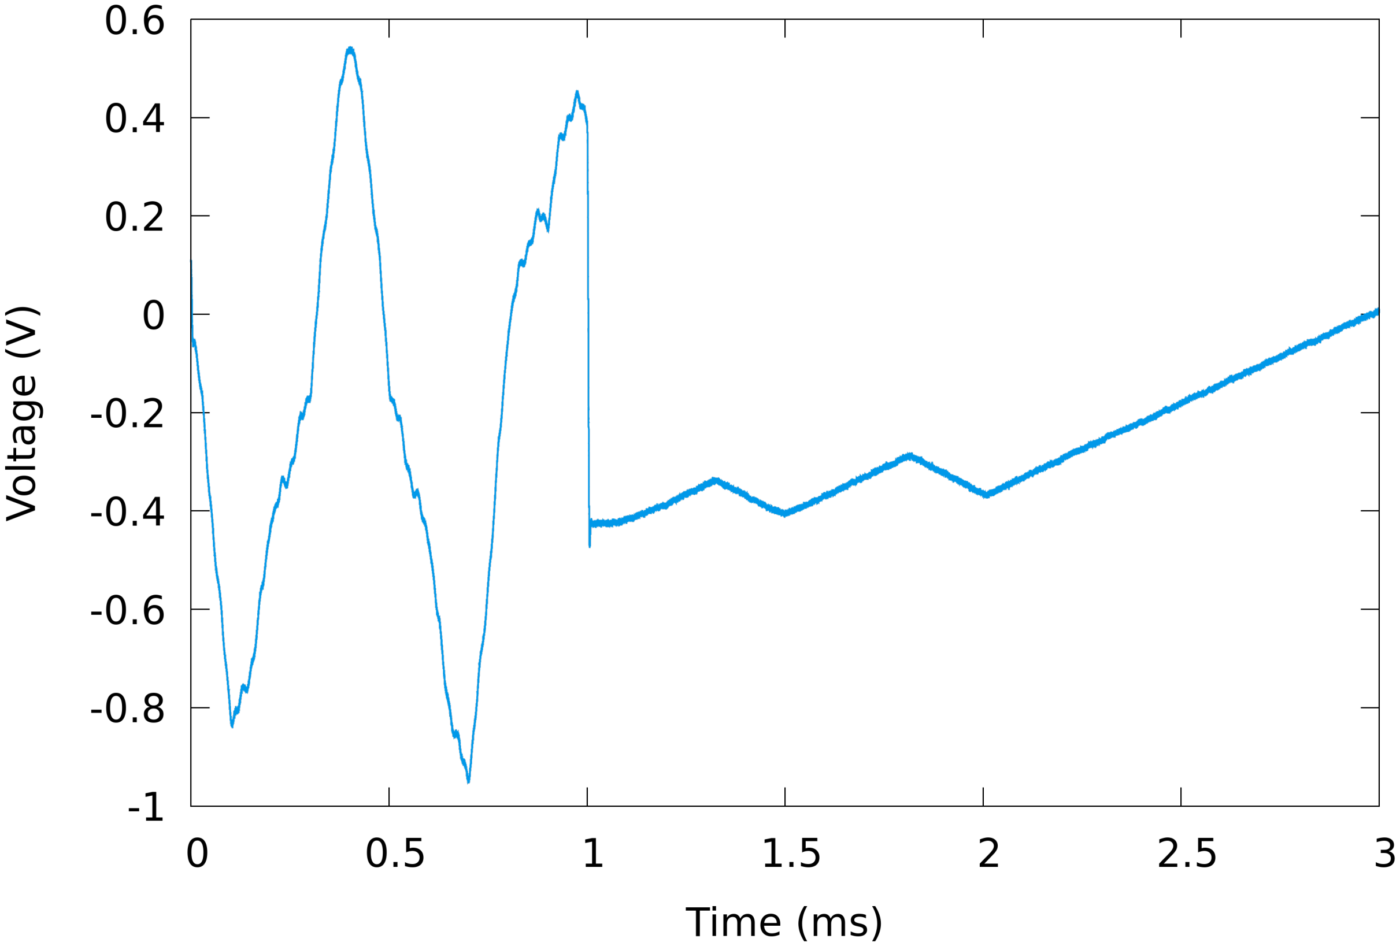
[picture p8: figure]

Figure 1: Paper, color version.

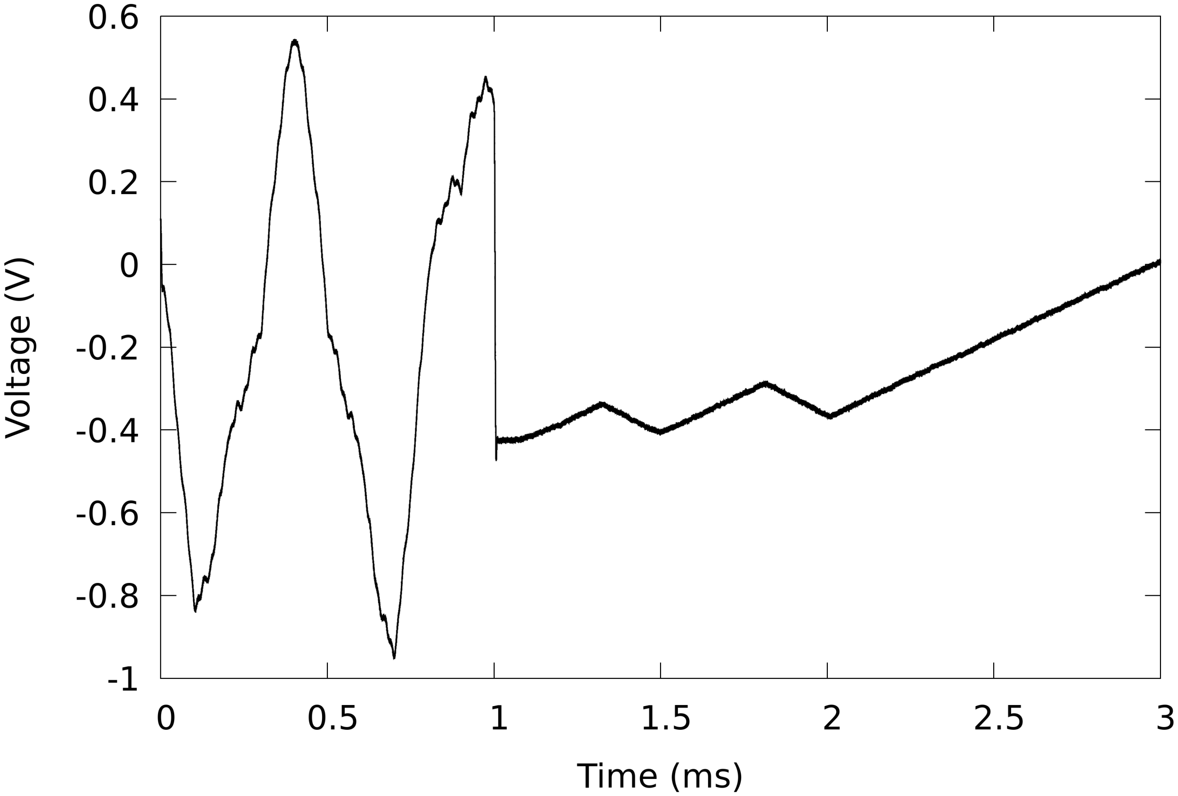
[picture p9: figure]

Figure 2: Paper, grayscale version.

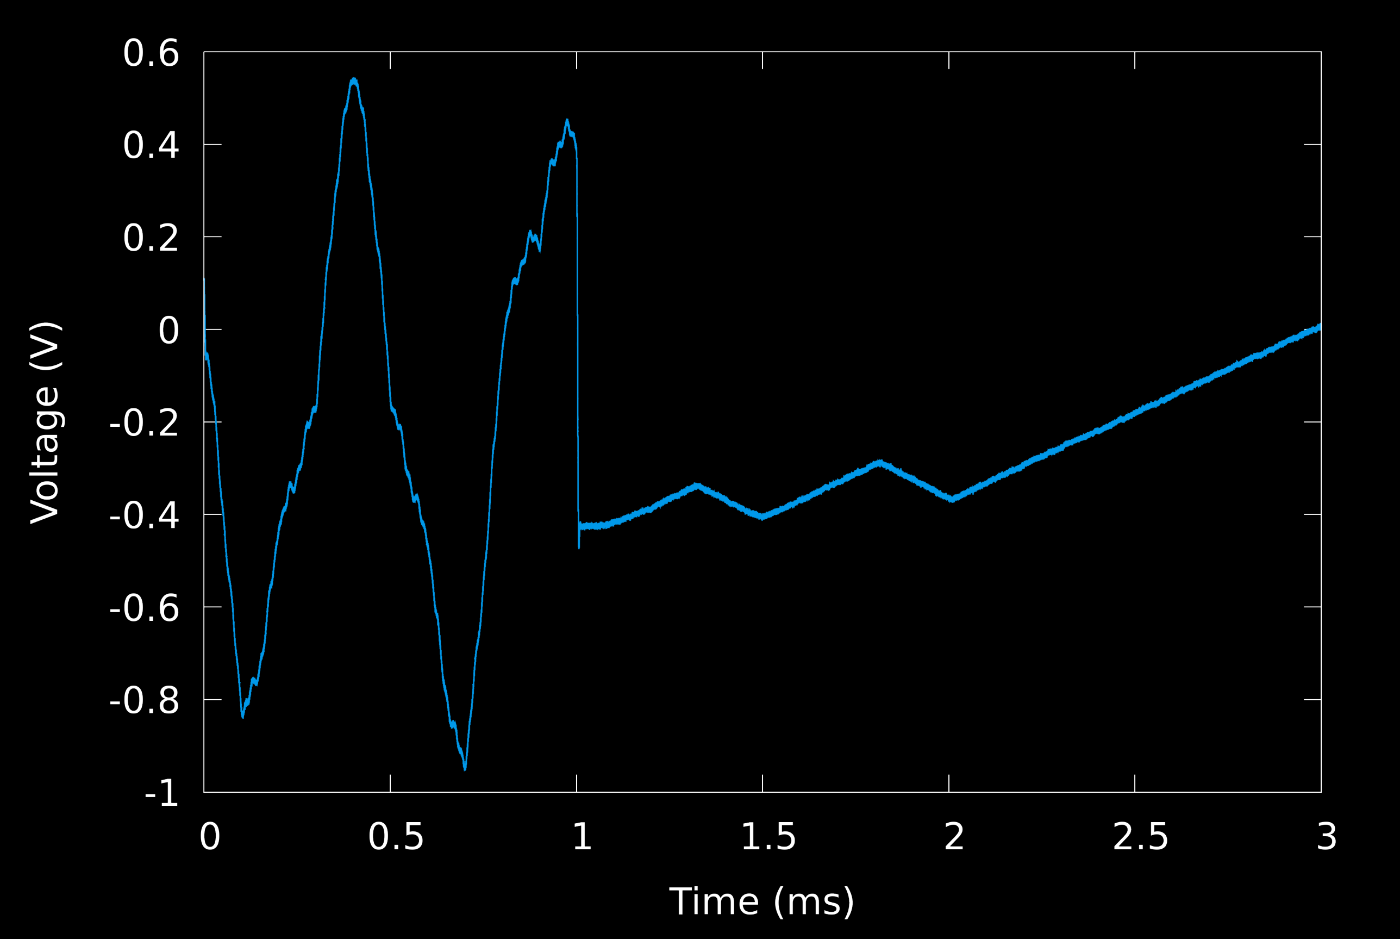
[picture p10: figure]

Figure 3: Dark Owl version (beamer slides).

set terminal pngcairo transparent enhanced font "Droid Sans,72" \ fontscale 1.0 size 3600, 2400

# Dark Owl

text = '#ffffff'
spcolor = '#0098e9' # OwlBlue set output 'spumpus-do.png'

# Paper Color

# text = '#000000'

# spcolor = '#0098e9' # OwlBlue # set output 'spumpus-pc.png'

# Paper Grayscale

# text = '#000000'

# spcolor = '#000000'

# set output 'spumpus-pg.png'

set style increment default

set border lw 3 lc rgb text

set xlabel tc rgb text
set ylabel tc rgb text

set datafile separator ',' sphist = 'spumpus-hist.csv' spout = 'spumpus-out.csv'

unset key
set xlabel 'Time (ms)'
set ylabel 'Voltage (V)'
set xrange [0:3] noreverse writeback

plot \
| sphist u ($1 * 1e3):($2) w lines lw 4 lt rgb spcolor

# FIFO P3F Arduino Due Code

## Alex Striff

## August 26, 2018

/******************************************************************************* * Time Delay Device Arduino Control
* Edgar Perez and Alex Striff
* Reed College Physics Department
*
* For more information, contact Lucas Illing <illing@reed.edu>.
*
* Version | Date | Author | Changes
* ------- | ---------- | ----------- | -------------------------------------------
* v1.0 | 2016-12-15 | Edgar Perez | Prototype completed.
* v2.0 | 2019-07-XX | Alex Striff | Modified for publication board.
*
******************************************************************************/

// Code options (feature selection)
#define SCREEN // Uncomment to enable screen output

#define SCONTROL // Uncomment for serial control and logging

#define HISTORY | // Uncomment for FIFO initial state programming (req: SCONTROL)

#define DEBUG | // Uncomment for serial debug output

#if defined(HISTORY) && defined(SCONTROL)

#define HIST

#include <CRC32.h>

#endif

#ifdef SCREEN

#include <Wire.h>

#include <Adafruit_GFX.h>

#include <Adafruit_SSD1306.h>

// #include <Fonts/FreeSans9pt7b.h>
#include "lato24.h"

#define DIGIT_FONT | &Lato_Regular_24 // 24 px high

#define TEXT_FONT | NULL | // 8 px high, NULL for default font in Adafruit GFX

extern TwoWire Wire1; // Use second I2C pins on the Due

#define SCREEN_WIDTH 128 // OLED display width, in pixels

#define SCREEN_HEIGHT 32 // OLED display height, in pixels

#define OLED_RESET A0 // Reset pin (or -1 if sharing Arduino reset pin) Adafruit_SSD1306 display(SCREEN_WIDTH, SCREEN_HEIGHT, &Wire1, OLED_RESET); boolean screen = true;

boolean draw = true;
char s_digits[16];

enum menu_mode {
MENU = 0, // Main menu
DELAY, | // Adjust the word count using the rotary encoder
FIFO, | // Show FIFO status
MENU_MODES,
} menu_mode = DELAY;

const PROGMEM char menu_names[][16] = { "Menu",
"Delay",
"FIFO",
};

uint32_t menu_pos = MENU + 1; int menu_press = 0;

// Double-press parameters int dpress = 0;
long dpress_delay = 100L;
long dpress_time = 0L;

// Repeated drawing parameters (in ms) long last_update = 0L;
long update_interval = 100L;

#endif // SCREEN

typedef const uint8_t pin;

typedef struct {
pin p; | // The pin that the button is connected to.
long debounce_delay; | // The delay (ms) for debouncing a button press.
int state; | // The current state of the button.
int last_state; | // The last state of the button.
long last_debounce_time; | // The last debounce time for the button.
} button;

typedef struct {
pin a; | // Output A
pin b; | // Output B
button btn; | // Button (knob of encoder)

} rotary_encoder;

// FIFO word limits
// min_words = 1 or 2 give the same delay.
// min_words = 3 is off-by-one depending upon the clock.
// FIFO words: | 0 | 1 | 2 | 3 | 4 | 5 | ...
// Delay words: invalid | 8 | 8 | 9,10 | 11 | 12 ...
const uint32_t min_words | = 4; // FIFO flags
const uint32_t max_words | = 262144; // FIFO flags
const uint32_t off_words | = 3 + 2 + 2; // ADC + DAC + FIFO.
const uint32_t init_words = 100; // FIFO + offset (user-visible)

#ifdef HIST

// History programming buffer
#define HBUF_SIZE | 16 // Make hist relatively large, given SRAM limitations

byte hist[HBUF_SIZE]; | // Holds (HBUF_SIZE / 2) code words (uint16_t)
#endif // HIST

// Rotary encoder pin mapping
rotary_encoder enc = {
.a | = 48, // ENC_A pin
.b | = 50, // ENC_B pin
.btn = {
.p = 52, // ENC_BTN pin
.debounce_delay = 50,
.state = 0,
.last_state = 0,
.last_debounce_time = 0
}
};

uint32_t words; // The number of delay words for the FIFO uint32_t words_digit = 0;

int32_t | count_min = min_words;
int32_t | count_max = max_words;
int32_t | count_mul = 1000;

// FIFO pin mappings:
// Active LOW unless stated otherwise
pin RT | = 42;
pin OE | = 45;
pin REN | = 43;
pin OR | = 40;
pin PAE | = 41;
pin HF | = 38;
pin PAF | = 39;
pin FWFT | = 37; // FWFT/SI. Active HIGH

pin IR | = 36;
pin LD | = 34;
pin MRS | = 35;
pin PRS | = 32;
pin WEN | = 31;
pin SEN | = 30;

// Clock control pin mappings:
// Active HIGH unless stated otherwise
pin nPROG | = 22;
pin CLK1 | = 26; // 1CLK (single-clock operation)
pin WCLK_S = 24;
pin ADC_CLK_S = 28;
pin PROG_D = DAC1;
pin STRIG = 33;

// FIFO flags to show in status. All active low. enum fifo_flag {
F_IR = 0, // Input ready
F_OR, | // Output ready
F_PAF, | // Partially almost full
F_PAE, | // Partially almost empty
F_HF, | // Half full
F_SIZE, | // The number of flags (not on FIFO)
} fifo_flags;

const pin fifo_flag_pins[] = {
IR,
OR,
PAF,
PAE,
HF,
};

const PROGMEM char fifo_flag_names[][16] = { "IR",
"OR",
"PAF",
"PAE",
"HF",
};

// DAC pin mapping
pin DAC_LDAC = 46;
pin DAC_CS = 44;

// Serial command buffer
#ifdef SCONTROL

#define SBLEN 16

char sb[SBLEN];
#endif // SCONTROL

void setup(void)
{
// Serial communication
Serial.begin(115200);
Serial.print(F(
"====================\n"
" FIFO_P3 Time Delay \n"
"====================\n"
" | Reed College | \n"
" Physics Department \n"
" | 2019 | \n"
"====================\n"
" | Alex Striff | \n"
" | Edgar Perez | \n"
" | Lucas Illing | \n"
"====================\n"
"Enabled features: "
#ifdef DEBUG

"DEBUG "
#endif // DEBUG

#ifdef SCREEN

"SCREEN "
#endif // SCREEN

#ifdef SCONTROL

"SCONTROL "
#endif // SCONTROL

#ifdef HIST

"HIST "
#endif // HIST

"\n"
"Type 'h' for help.\n\n"
"Setting up I/O ... "
));

// DAC initialization
delay(10);
digitalWrite(nPROG, LOW); // x. Check not flipped digitalWrite(DAC_LDAC, HIGH);
delay(5);
digitalWrite(nPROG, HIGH); // x. digitalWrite(DAC_LDAC, LOW);

// Due (self) DAC initialization analogWriteResolution(12);
pinMode(PROG_D, OUTPUT);
analogWrite(PROG_D, 1u << (12 - 2)); // Half full scale

// Clock control pins
pinMode(nPROG, | OUTPUT);
pinMode(CLK1, | OUTPUT);
pinMode(WCLK_S, | OUTPUT);
pinMode(ADC_CLK_S, OUTPUT);
pinMode(STRIG, | OUTPUT);

// Clock default state (single clock, not programming)
digitalWrite(CLK1, | HIGH);
digitalWrite(WCLK_S, | LOW);
digitalWrite(ADC_CLK_S, LOW);
digitalWrite(STRIG, | LOW);

digitalWrite(nPROG, HIGH); // Disable operation while setting up.

// FIFO pins
pinMode(REN, | OUTPUT);
pinMode(OR, | INPUT_PULLUP);
pinMode(PAE, | INPUT_PULLUP);
pinMode(HF, | INPUT_PULLUP);
pinMode(PAF, | INPUT_PULLUP);
pinMode(IR, | INPUT_PULLUP);
pinMode(OE, | OUTPUT);
pinMode(RT, | OUTPUT);
pinMode(FWFT, OUTPUT);
pinMode(LD, | OUTPUT);
pinMode(MRS, | OUTPUT);
pinMode(PRS, | OUTPUT);
pinMode(WEN, | OUTPUT);
pinMode(SEN, | OUTPUT);

// FIFO default states
digitalWrite(MRS, | HIGH);
digitalWrite(PRS, | HIGH);
digitalWrite(RT, | HIGH);
//digitalWrite(FWFT, HIGH); digitalWrite(FWFT, LOW); // Let's try IDT mode
digitalWrite(LD, | HIGH);
digitalWrite(WEN, | HIGH);
digitalWrite(REN, | HIGH);
digitalWrite(SEN, | HIGH);
digitalWrite(OE, | LOW);

// DAC pins

delay(100);
pinMode(nPROG, OUTPUT);
pinMode(DAC_LDAC, OUTPUT); pinMode(DAC_CS, OUTPUT);

// More DAC initialization delay(10);
pinMode(DAC_CS, OUTPUT);
digitalWrite(DAC_CS, HIGH); delay(5);
digitalWrite(DAC_CS, LOW); delay(5);
digitalWrite(DAC_CS, HIGH); delay(5);
digitalWrite(DAC_CS, LOW); delay(10);

// Rotary encoder pins
pinMode(enc.btn.p, INPUT_PULLUP);
pinMode(enc.a, | INPUT_PULLUP);
pinMode(enc.b, | INPUT_PULLUP);
read_encoder(&enc); // Read to initialize previous quadrature state.

// Screen initialization
#ifdef SCREEN

if (!display.begin(SSD1306_SWITCHCAPVCC, 0x3C)) { // Address 0x3C for 128x32 Serial.println(F("SSD1306 allocation failed. Unable to use screen.")); screen = false;
} else {
screen = true;
display.clearDisplay();
display.cp437(true);
display.setTextColor(WHITE); display.setTextSize(1);
display.setCursor(0, 0);
display.print(F("Time Delay Device vP3")); display.setCursor(0, 8);
display.print(F("Reed College Physics")); display.setCursor(0, 24);
display.print(F("2-press knob for menu")); display.display();

for (uint8_t i = 0; i < SCREEN_WIDTH; i++) { display.drawPixel(i, 16 + (i*i / 7) % 8, WHITE); display.display();
}
}
#endif // SCREEN

// Do a master reset to initialize the FIFO Serial.print(F(" complete. Initializing FIFO:\n\t")); delay(5);
master_reset(false);
Serial.println();
set_delay(init_words, true); }

void loop(void)
{
uint32_t narg;

#ifdef SCONTROL

for (int i = 0; i < SBLEN; i++) sb[i] = '\0';

// TODO: Update help.
if (Serial.available() > 0) { Serial.readBytesUntil(';', sb, SBLEN);

narg = atol(sb + 2);
switch (sb[0]) {
case 'h': // Fallthrough.
case 'H': // Fallthrough.
case '?': serial_help(); break; case 'm':
switch (sb[1]) {
case 'r': master_reset(true); break; default: unknown(); break;
}
break;
case 'p':
switch (sb[1]) {
case 'r': partial_reset(true); break; #ifdef DEBUG
case 'p': prog_debug(); break;
case 'c': prog_clock_debug(); break; #endif // DEBUG
#ifdef HIST

case 'h': prog_hist(narg); break; #endif // HIST
default: unknown(); break;
}
break;
case 'd': set_delay(narg, true); break; #ifdef HIST

case 'g':
switch (sb[1]) {
case 'o': start(); break;
default: unknown(); break; }
break;
#endif // HIST

case 'c':
switch (sb[1]) {
case '1': single_clock(); break; case '2': dual_clock(); break; default: unknown(); break;
}
break;
case 's': report_status(); break; case 'x': pause(narg); break; case 'i': initialize(); break; case 'q': quit(); break;
default: unknown(); break;

}
}
#endif // SCONTROL

#ifdef SCREEN

if (screen) {
switch (menu_mode) {
case MENU:
menu_pos = enc_adjust_nodigit(&menu_pos, MENU + 1, MENU_MODES - 1, true); if (draw) {
display.clearDisplay();
display.setFont(TEXT_FONT);
for (size_t i = MENU + 1; i < MENU_MODES; i++) { int16_t x = 8 + ((i - 1) / 4) * SCREEN_WIDTH; int16_t y = ((i - 1) % 4) * 8; display.setCursor(x, y);
display.print(menu_names[i]);
}

int16_t alt = ((menu_pos - 1) / 4) * SCREEN_WIDTH; int16_t mid = 2 + ((menu_pos - 1) % 4) * 8; display.fillTriangle(alt, mid - 2, alt, mid + 2, alt + 3, mid, WHITE);
display.display();
draw = false;
}

if (read_button(&(enc.btn))) {
menu_press = 1;
} else if (menu_press == 1) {
// button was pressed and now it is not menu_mode = (enum menu_mode) menu_pos; menu_press = 0;
draw = true;
}

break;

case DELAY:
{ // Surrounding block to disambiguate scope set_delay(enc_adjust(&words, &words_digit, count_min, count_max, false, false), true); int16_t x, y;
uint16_t w, h;
int16_t digit_x = 0;
int16_t digit_y = 24;

draw |= millis() - last_update >= update_interval; if (draw) {
display.clearDisplay();
sprintf(s_digits, "%06u", words + off_words); display.setFont(DIGIT_FONT); display.setCursor(digit_x, digit_y); display.print(s_digits);

int16_t mid = 6 + (6 - words_digit - 1) * 15;
int16_t base = 31;
display.fillTriangle(mid - 3, base, mid + 3, base, mid,
| base - 4, WHITE);

display.setFont(TEXT_FONT); display.getTextBounds(s_digits, digit_x, digit_y, &x,
| &y, &w, &h);
display.setCursor(SCREEN_WIDTH - w + 6,
| digit_y - 2*h + 1);
display.print(F("Delay")); display.getTextBounds(s_digits, digit_x, digit_y,
| &x, &y, &w, &h);
display.setCursor(SCREEN_WIDTH - w + 6,
| digit_y - h + 1);
display.print(F("words"));

display.display();
draw = false;
}

}
break;

case FIFO:
{
draw |= millis() - last_update >= update_interval; if (draw) {
display.clearDisplay();
display.setFont(TEXT_FONT);
for (size_t i = 0; i < F_SIZE; i++) { int16_t x = 8 + (i / 4)
* SCREEN_WIDTH / ((F_SIZE / 4) + 1); int16_t y = (i % 4) * 8;
display.setCursor(x, y);
display.print(fifo_flag_names[i]); display.setCursor(x + 4*8, y);
// Invert to show understandable logic display.print(digitalRead(fifo_flag_pins[i]) ? 0 : 1, DEC);
}
display.display();
draw = false;
last_update = millis();
}

press_menu_return(&enc);
}
break;

default:
Serial.println("Menu error!"); break;
}

// Double-press detection
if (menu_mode != MENU) {
int press = read_button(&(enc.btn));
int quick = millis() - dpress_time <= dpress_delay; if ((dpress == 0 && press)
|| (dpress == 1 && !press && quick)
|| (dpress == 2 && press && quick)) { dpress_time = millis();
dpress++;
} else if (dpress == 3 && !press && quick) { dpress = 0;
menu_mode = menu_mode != MENU ? MENU : DELAY; draw = true;
} else if (!quick) {

dpress = 0;
}
}
}
#endif // SCREEN

}

#ifdef SCREEN

void press_menu_return(rotary_encoder *e) {
if (read_button(&(e->btn))) {
menu_press = HIGH;
} else if (menu_press == HIGH) { // Button was pressed and now it is not menu_press = LOW;
menu_mode = MENU;
menu_press = LOW;
draw = true;
}
}
#endif // SCREEN

#ifdef SCONTROL

void unknown(void)
{
Serial.println(F("Unknown Command. Type 'h' for help.")); serial_help();
}
#endif // SCONTROL

#ifdef SCONTROL

void serial_help(void)
{
Serial.print(F(
"Time Delay Device Serial Commands\n" "=================================\n"
"mr\tPerforms a master reset of FIFO memory.\n"
"pr\tPerforms a partial reset of FIFO memory.\n"
"d N\tSets delay to N words, where N is a decimal number between ")); Serial.print(min_words + off_words, DEC);
Serial.print(F(" and "));
Serial.print(max_words + off_words, DEC);
Serial.print(F(
".\n"
"\tE.g.: 'd 9' and 'd 101' produce delays of 9 and 101 words, respectively.\n" "\tValues outside the possible range will be clamped, so 'd 0' is the same as 'd " ));
Serial.print(min_words + off_words, DEC);

Serial.print(F(
"'.\n"
"\t<time delay> = <delay words> * <clock period>.\n"
"ph N;<data>\tPrograms N words of initial history into the FIFO.\n" "\tAfter the semicolon, 2N bytes of big-endian data must follow.\n" "\tThe data are 12-bit unsigned code words representing analog signals,\n" "\twhere 0x0000 gives -2.5V and 0x0FFF gives +2.5V.\n"
"s\tReports FIFO status.\n"
"x N\tPauses for N seconds (neglecting serial delays; not precise).\n" "i\tInitializes the program.\n"
"q\tQuits the program.\n"
"h H ?\tShows this help.\n"
"\n"
));
}
#endif // SCONTROL

void partial_reset(boolean start)
{
long t1, t2;
Serial.print(F("Partial Reset ... ")); t1 = micros();
digitalWrite(nPROG, LOW);
delay(1);

digitalWrite(REN, HIGH);
digitalWrite(WEN, HIGH);
digitalWrite(RT, HIGH);
delayMicroseconds(3);
digitalWrite(PRS, LOW);
delayMicroseconds(3);
digitalWrite(PRS, HIGH);
delayMicroseconds(3);
digitalWrite(WEN, LOW);
if (start) digitalWrite(nPROG, HIGH);

t2 = micros() - t1;
delayMicroseconds(1);
Serial.print("done (");
Serial.print(t2);
Serial.println(" us).");
}

void master_reset(boolean start) {
long t1, t2;

Serial.print(F("Master Reset ... ")); t1 = micros();
digitalWrite(nPROG, LOW);
//digitalWrite(FWFT, HIGH); digitalWrite(FWFT, LOW); // Let's try IDT mode
digitalWrite(LD, | HIGH);
digitalWrite(MRS, | LOW);
delayMicroseconds(1);
digitalWrite(MRS, HIGH);
if (start) digitalWrite(nPROG, HIGH);

t2 = micros() - t1;
delayMicroseconds(1);
Serial.print(F("done ("));
Serial.print(t2);
Serial.println(F(" us)."));
Serial.print(F("Device in FWFT with Serial Loading.\n")); }

#ifdef SCONTROL

void report_status(void)
{
Serial.print(F(
"FIFO Status\n"
"===========\n"));

for (size_t i = 0; i < F_SIZE; i++) { Serial.print(F("~"));
Serial.print(fifo_flag_names[i]); Serial.print(F("\t"));
Serial.println(digitalRead(fifo_flag_pins[i]), DEC); }
Serial.println();

#ifdef DEBUG

Serial.println(words_digit); Serial.println(words + off_words); Serial.println(ipow(3, 0)); Serial.println(ipow(3, 1)); Serial.println(ipow(3, 5)); #endif // DEBUG
}
#endif // SCONTROL

#ifdef SCONTROL

void pause(uint32_t n)

{
for (uint32_t i = 0; i < n; i++) { Serial.println(n - i);
delay(1000);
}
Serial.println("0.");
}
#endif // SCONTROL

void set_delay(uint32_t n, boolean start) {
unsigned int m;
int bits;

n = clamp(n - off_words, min_words, max_words); if (n == words && start) return;
words = n;
m = max_words - n;

Serial.print(F("Sending a ")); Serial.print(n);
Serial.print(F("-word delay ... ")); digitalWrite(nPROG, 0);
delayMicroseconds(10);

digitalWrite(WCLK_S, 0);
digitalWrite(LD, 0);
digitalWrite(SEN, 0);
delayMicroseconds(2);

// The following number is defined because PAF triggers at the given // number of words AWAY FROM the end, not AT the given word like PAE. for (int i = 0; i < 36 ; i++) {
bits = i == 0 ? 1 : bitRead(m, i - 18);
digitalWrite(FWFT, bits);
delayMicroseconds(1);
digitalWrite(WCLK_S, 1);
delayMicroseconds(1);
digitalWrite(WCLK_S, 0);
}

digitalWrite(LD, 1);
digitalWrite(SEN, 1);
digitalWrite(nPROG, 1);
Serial.print(F("done. Resetting: ")); partial_reset(start);
}

void set_fifo_delay(uint32_t n, boolean start) {
set_delay(n + off_words, start);
}

void initialize(void)
{
digitalWrite(WEN, 0);
digitalWrite(REN, 0);
Serial.println(F("Initiated program.")); }

void quit(void)
{
digitalWrite(WEN, 1);
digitalWrite(REN, 1);
Serial.println(F("Quit program.")); }

int read_encoder(rotary_encoder *e) {
static int8_t enc_states[4][4] = {
{ 0, -1, | 1, | 0},
{ 1, | 0, | 0, -1},
{-1, | 0, | 0, | 1},
{ 0, | 1, -1, | 0}
};
static uint8_t old_AB = 0;
int8_t direction;
uint8_t AB = digitalRead(e->a) << 1 | digitalRead(e->b);

direction = enc_states[old_AB][AB];
old_AB = AB;

return direction;
}

int32_t clamp(int32_t x, int32_t min, int32_t max) {
return x <= min ? min : x >= max ? max : x;
}

int ipow(int base, unsigned int exp) {
int result = 1;

for (; exp; base *= base, exp >>= 1) if (exp & 1)
result *= base;

return result;
}

uint32_t enc_adjust(uint32_t *n, uint32_t *digit, uint32_t n_min, uint32_t n_max, boolean reverse, boolean dreverse) {
int | direction;
int32_t count = *n;
direction = read_encoder(&enc);

if (direction) {
| if (read_button(&(enc.btn))) { *digit = clamp(*digit + direction * (dreverse ? -1 : 1), 0, 5);
| #ifdef DEBUG Serial.print(F("Button press: ")); Serial.println(*digit); #endif // DEBUG } else { count = clamp(count + direction * (reverse ? -1 : 1) * ipow(10, *digit), n_min, n_max);
| #ifdef DEBUG Serial.print(F("Count: ")); Serial.println(count); #endif // DEBUG

}
| #ifdef SCREEN draw = true; dpress = 0; #endif // SCREEN

}

return (uint32_t) count + off_words; }

uint32_t enc_adjust_nodigit(uint32_t *n, uint32_t n_min, uint32_t n_max, boolean reverse)
{

int | direction;
int32_t count = *n;
direction = read_encoder(&enc) * (reverse ? -1 : 1);

if (direction) {
| count = clamp(count + direction, n_min, n_max);
| #ifdef DEBUG Serial.print("ND Count: "); Serial.println(count); #endif // DEBUG
| #ifdef SCREEN draw = true; dpress = 0; #endif // SCREEN

}

return (uint32_t) count;
}

int read_button(button *button)
{
int reading = digitalRead(button->p);

if (reading != button->last_state)
button->last_debounce_time = millis();
if (millis() - button->last_debounce_time > button->debounce_delay) button->state = reading;

return button->last_state = reading;
}

#ifdef HIST

int prog_hist(uint32_t n)
{
// Reads n code words (uint16_t values for DAC) and programs them into the // FIFO memory. Little-endian.
uint32_t nwords = n;
n *= 2; // Words to bytes.
uint32_t bufs = 0u;
uint32_t bytes = 0u;
uint32_t col = 8;
uint32_t cols = 2;
uint32_t row = col * cols; char hex[16];
byte msb, lsb, sbyte;
uint16_t data;

uint32_t read_bytes;
uint32_t buf_remaining;
uint32_t adc_off = 3u;
uint32_t adc_ins = 0u;
CRC32 crc;

// Enter programming mode. digitalWrite(nPROG, LOW);
digitalWrite(STRIG, LOW);
Serial.print(F("Programming ")); Serial.print(nwords, DEC);
Serial.print(F(" words of history...\n\n")); master_reset(false);
//set_fifo_delay(nwords, false); set_delay(nwords, false);

// Program the data one hist[] buffer at a time. while (bytes < n) {
while (!Serial.available());

buf_remaining = min(HBUF_SIZE, n - bytes); read_bytes = Serial.readBytes(hist, buf_remaining); bytes += read_bytes;
boolean last = read_bytes < HBUF_SIZE;

if (read_bytes != buf_remaining) {
Serial.print(F("Error reading history data! (Received ")); Serial.print(bytes, DEC);
Serial.print(F(" bytes, but expected "));
Serial.print(n, DEC);
Serial.println(F(" bytes.)"));
return 0;
}

digitalWrite(ADC_CLK_S, LOW);
digitalWrite(WCLK_S, LOW);
for (uint32_t j = 0; j < (read_bytes / row) + (last ? 1 : 0); j++) { uint32_t end_bytes = last ? read_bytes % row : row;

// The actual programming
for (uint32_t k = 0; k < end_bytes; k++) {
// This may be decreased, depending upon signal speed delayMicroseconds(100);
sbyte = hist[row*j + k];
crc.update(sbyte);
if (k % 2 == 0) {
lsb = sbyte;
} else {

msb = sbyte;
// Programming circuitry inverts, so reinvert
data = 0x0FFF - ((msb << 8) | lsb);
//data = ((msb << 8) | lsb); // Inverted
analogWrite(PROG_D, data);
// This may be decreased, depending upon signal speed delayMicroseconds(1000);
// Write ADC output N-3 to the FIFO before latching in // the next in put to the ADC.
if (adc_ins >= adc_off) digitalWrite(WCLK_S, HIGH); // These microsecond delays are probably unnecessary. // Check FIFO clock hold times. delayMicroseconds(10);
if (adc_ins >= adc_off) digitalWrite(WCLK_S, LOW); delayMicroseconds(10);
digitalWrite(ADC_CLK_S, HIGH); delayMicroseconds(10);
digitalWrite(ADC_CLK_S, LOW);
if (adc_ins < adc_off) adc_ins++; }
}
// The last 3 (adc_off) history data words remain in the ADC. // They will be clocked in after the switch to normal operation // (external WCLK).

// Printing a hexdump back
sprintf(hex, "%06X:\t", bufs * HBUF_SIZE + j * row); Serial.print(hex);
for (uint32_t k = 0; k < end_bytes; k++) { sprintf(hex, "%02X", hist[row*j + k]); Serial.print(hex);
if (k % col == col - 1) Serial.print(' ');
}
if (last) { // Pad last row
for (uint32_t k = 0; k < 2 * (row - end_bytes); k++) Serial.print(' ');
}
Serial.print('\t');
for (uint32_t k = 0; k < end_bytes; k++) { byte b = hist[row*j + k];
Serial.print(b < 32 ? '.' : (char) b); }
Serial.println();
}

bufs++;
}
Serial.print(F("CRC32: "));

Serial.println(crc.finalize(), HEX); Serial.println(F(
"\nDone programming history." "Waiting for start command ('go')."));

return 1;
}
#endif // HIST

#ifdef HIST

void start()
{
// Start normal delay operation after programming the history. digitalWrite(nPROG, HIGH);
digitalWrite(STRIG, HIGH);
Serial.print(F("Started."));
}
#endif // HIST

#ifdef SCONTROL

void single_clock(void)
{
digitalWrite(CLK1, HIGH);
}
#endif // SCONTROL

#ifdef SCONTROL

void dual_clock(void)
{
digitalWrite(CLK1, LOW);
}
#endif // SCONTROL

void prog_debug(void)
{
uint32_t nwords = 1 << 13; digitalWrite(nPROG, LOW);
digitalWrite(STRIG, LOW);
Serial.print(F("DEBUG: Programming ")); Serial.print(nwords, DEC);
Serial.print(F(" words of history...\n\n")); master_reset(false);
set_fifo_delay(nwords, false); digitalWrite(nPROG, LOW);

delayMicroseconds(10);
// Does not account for first three words into ADC, but OK for debugging for (uint16_t triangle = 0u ;; triangle++) {
//for (uint16_t triangle = 0u; triangle < nwords; triangle++) {
// High 4 bits are discarded. Subtraction inverts. analogWrite(PROG_D, ((1<<12) - 1) - 4 * triangle); digitalWrite(WCLK_S, HIGH);
digitalWrite(WCLK_S, LOW); digitalWrite(ADC_CLK_S, HIGH); digitalWrite(ADC_CLK_S, LOW);
}
Serial.println(F(
"\nDEBUG: Done programming history." "Waiting for start command ('go').")); }

void prog_clock_debug(void)
{
digitalWrite(WCLK_S, HIGH); digitalWrite(WCLK_S, LOW); digitalWrite(ADC_CLK_S, HIGH); digitalWrite(ADC_CLK_S, LOW); }

// vim:ts=4:sts=4:sw=4:et:

5k1 | 3.3V R7 5k1 | GND Rotary Encoder | 1
7 Vcc | 8 U2 SN74LVC2G157_MUX_TI A

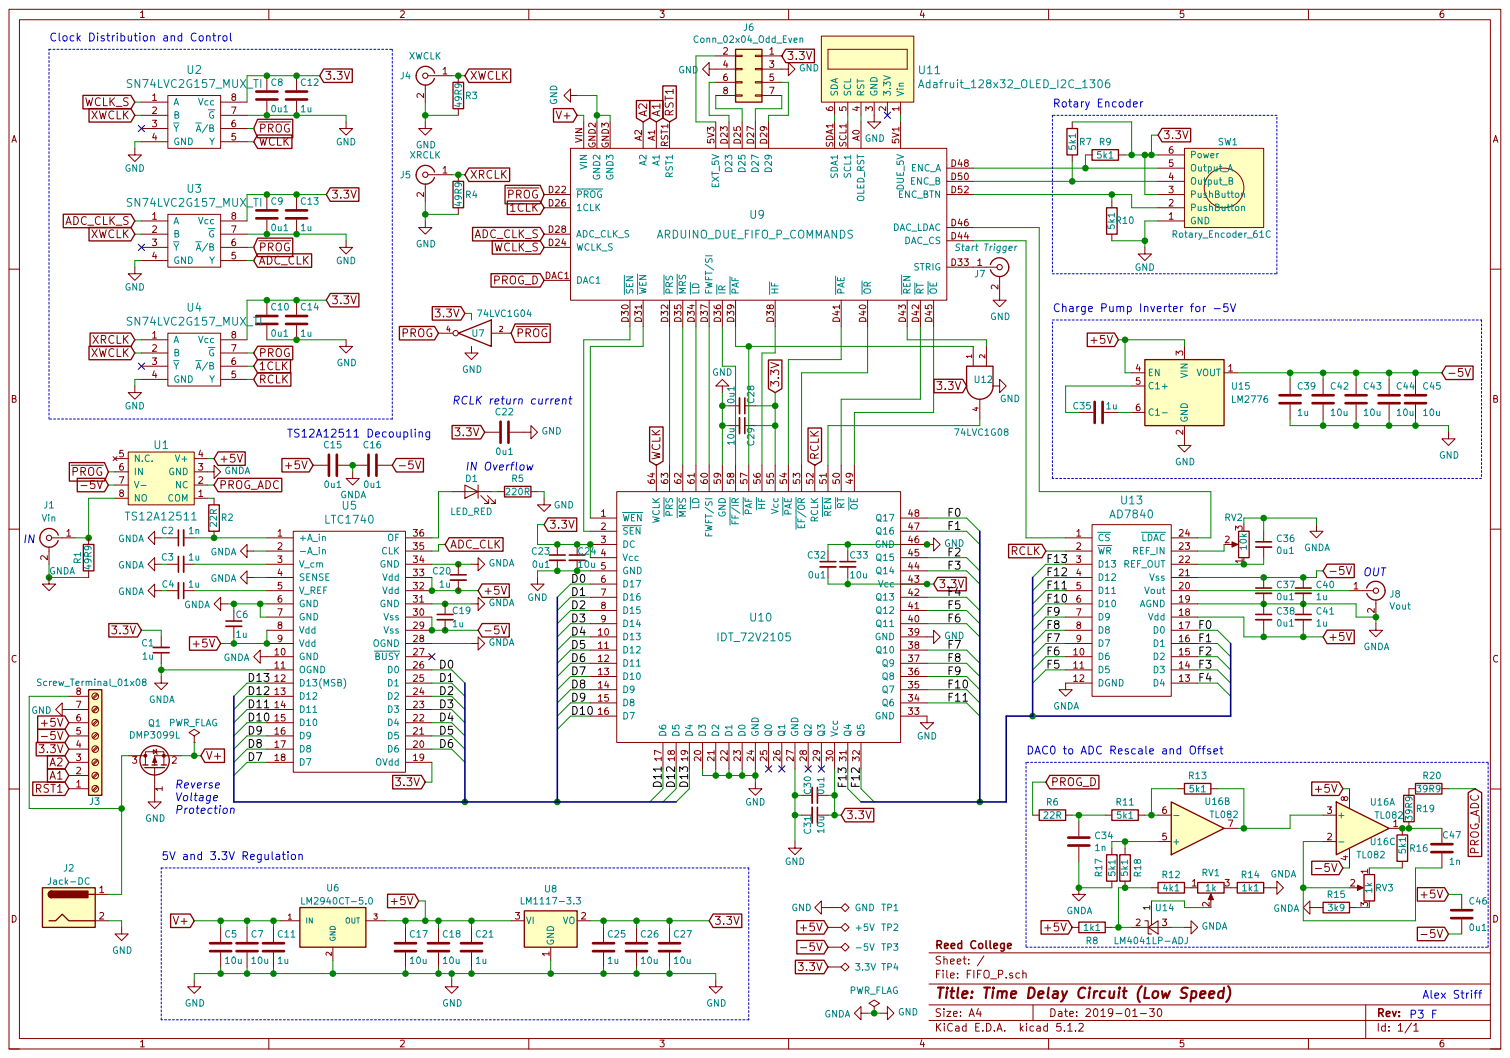
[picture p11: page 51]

6 U11Adafruit_128x32_OLED_I2C_1306 GND GND GNDA GNDA GNDA GNDA C17

File: FIFO_P.sch Sheet: / Reed College 3.3V

Id: 1/1 Title: Time Delay Circuit (Low Speed)

3V3 | C0 C1 C2 C3 C4 C5 C6 C7 C8 C9 C10 C11 Q11 | 1 CLK 10 | Reset 11 | Q8 | 12 Q7 | 13 Q9 | 14 Q10 | 15 VDD ¹⁶ | Q5 | 2 Q4 | 3 Q6 | 4 Q3 | 5 Q2 | 6 Q1 | 7 VSS
4040 RESET RESET | GND GND

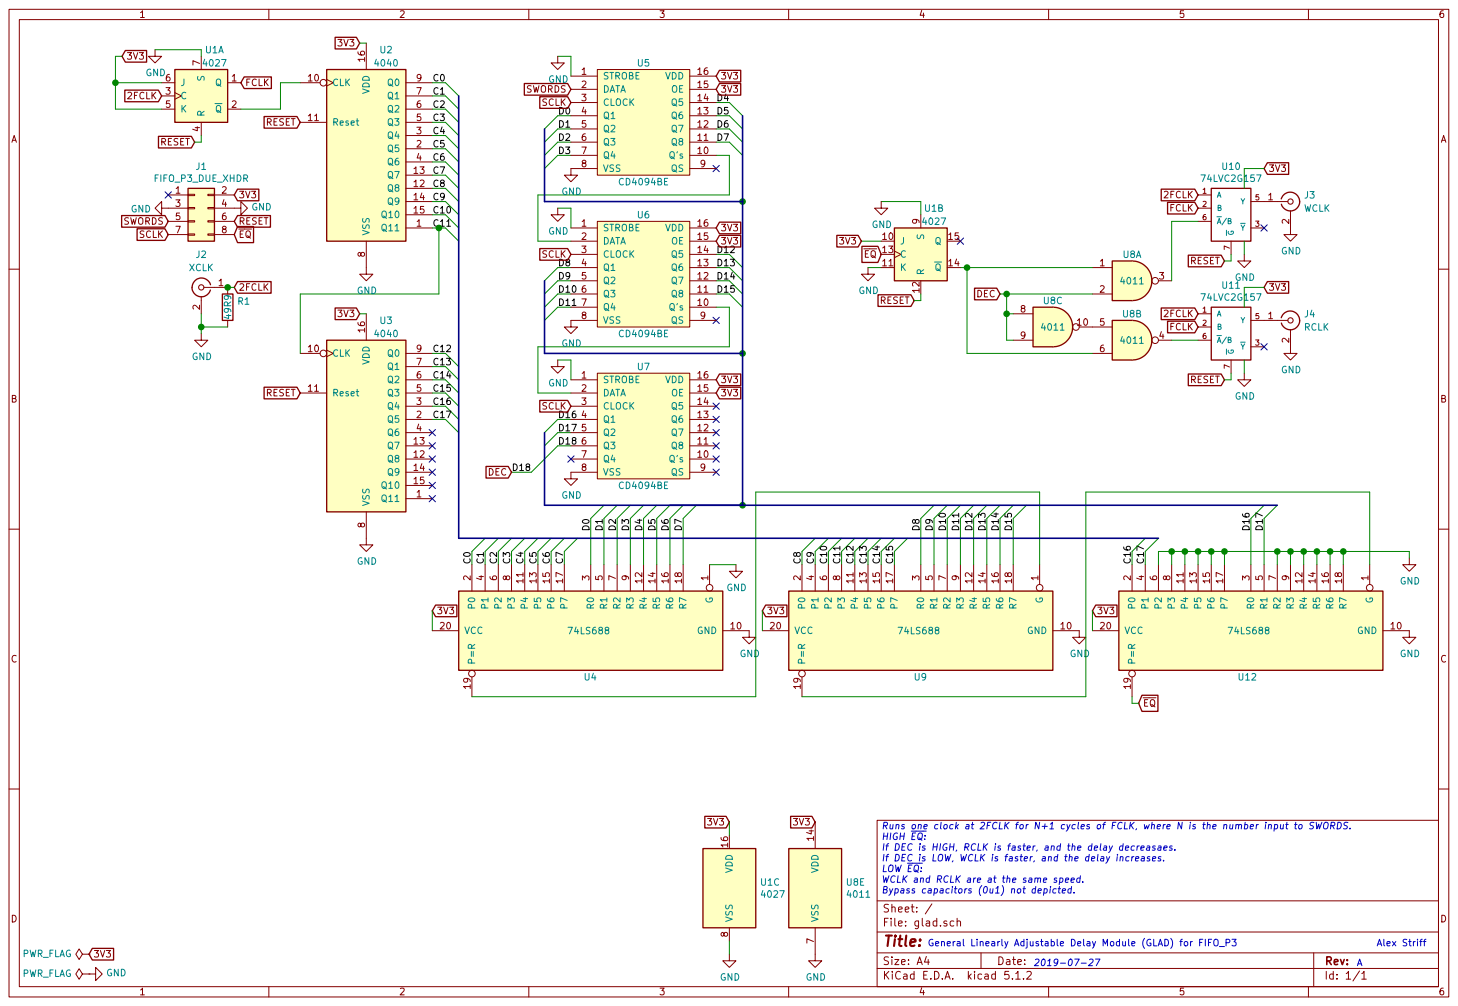
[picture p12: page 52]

Runs one clock at 2FCLK for N+1 cycles of FCLK, where N is the number input to SWORDS. HIGH EQ:

If DEC is HIGH, RCLK is faster, and the delay decreasaes.
If DEC is LOW, WCLK is faster, and the delay increases. LOW EQ: WCLK and RCLK are at the same speed.

Bypass capacitors (0u1) not depicted.
Id: 1/1 Title:

# Arbitrary Delay for Fifo P3F

Alex Striff

August 26, 2019

Since we can clock the read clock (RCLK) and write clock (WCLK) for the fifo independently, we can make the delay be an arbitrary function of state if

fwclk = kτ˙ + frclk

This may be achieved with the circuit of Fig. 1.
I have already ordered some prototype parts that could be used to create this circuit in hardware. They should be in the cardboard box of parts and stuff that I left in the lab.
- TL082 jfet-input opamps (on breakout boards).
- A vco (voltage-controlled oscillator) part by ti.
- A 4 MHz crystal oscillator.
- A binary ripple-counter part (cd-series).
- Some muxes (maybe on breakout boards).

We just need to use opamps to differentiate τ (y) and then suitably offset and scale that signal so that when τ˙ = 0 s s⁻¹
, the input voltage to the vco will cause the vco to generate a clock at frclk. Alternatively, make the differentiator inverting and switch the role of WCLK and RCLK.
τ (y) | t | k | Σ

V

VCO | fwclk

frclk

Figure 1: Arbitrary delay circuit block diagram.

1

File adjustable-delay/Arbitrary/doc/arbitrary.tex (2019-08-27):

\documentclass[11pt,letterpaper]{article}

\usepackage{amsmath,amssymb,amsthm}
\usepackage{graphicx}
\usepackage{siunitx}
\usepackage{microtype}
\usepackage{tikz}
\usetikzlibrary{arrows,positioning,fit,decorations.pathmorphing}

% Set nice colors for TikZ pictures (also good grayscale balance)
\definecolor{OwlRed}{RGB}{ 255, 92, 168}
\definecolor{OwlGreen}{RGB}{ 90, 168, 0}
\definecolor{OwlBlue}{RGB}{ 0, 152, 233}
\definecolor{OwlYellow}{RGB}{ 242, 147, 24}
\colorlet{OwlViolet}{OwlRed!50!OwlBlue}
\colorlet{OwlBrown}{OwlRed!50!OwlGreen}
\colorlet{OwlOrange}{OwlRed!50!OwlYellow}
\colorlet{OwlCyan}{OwlGreen!50!OwlBlue}
\colorlet{red}{OwlRed}
\colorlet{green}{OwlGreen}
\colorlet{blue}{OwlBlue}
\colorlet{yellow}{OwlYellow}
\colorlet{violet}{OwlViolet}
\colorlet{brown}{OwlBrown}
\colorlet{orange}{OwlOrange}
\colorlet{cyan}{OwlCyan}

\title{Arbitrary Delay for \textsc{Fifo} P3F}
\author{Alex Striff}
\date{August 26, 2019}

\begin{document}
\maketitle

Since we can clock the read clock (\texttt{RCLK}) and write clock
(\texttt{WCLK}) for the \textsc{fifo} independently, we can make the delay be an
arbitrary function of state if
\[
  \textcolor{yellow}{f_\textsc{wclk}}
  = k\textcolor{blue}{\dot{\tau}} + \textcolor{red}{f_\textsc{rclk}}
\]
This may be achieved with the circuit of Fig.~\ref{fig:arb}.

\begin{figure}
  \centering
  \begin{tikzpicture}[%
      isosceles triangle apex angle=60,
      block/.style={rectangle,fill=#1,draw=#1!90,thick,rounded corners=4pt},
      block/.default={blue},
      signal/.style={midway,font=\footnotesize},
      conn/.style={thick,->},
      ampblock/.style={block=#1,isosceles triangle},
      ampblock/.default={blue},
      circblock/.style={block=#1,circle},
      circblock/.default={blue},
    ]
    \node[block=blue] (delay) at (0,0) {$\tau(y)$};
    \node[block=violet] (dt) at (1.5,0) {$\dv{t}$};
    \node[ampblock=violet] (amp) at (3,0) {$k$};
    \node[circblock=violet] (add) at (5,0) {$\Sigma$};
    \node[block=violet] (off) at (5,-1.5) {$V$};
    \node[block=violet] (vco) at (7,0) {VCO};
    \node[block=yellow] (wclk) at (9.5,0) {$f_\textsc{wclk}$};
    \node[block=red] (rclk) at (9.5,-1.5) {$f_\textsc{rclk}$};
    \draw[conn] (delay) -- (dt);
    \draw[conn] (dt) -- (amp);
    \draw[conn] (amp.east)+(-3pt,0) -- (add);
    \draw[conn] (rclk) -- (off);
    \draw[conn] (off) -- (add);
    \draw[conn] (add) -- (vco);
    \draw[conn] (vco) -- (wclk);
  \end{tikzpicture}
  \caption{Arbitrary delay circuit block diagram.}
  \label{fig:arb}
\end{figure}

I have already ordered some prototype parts that could be used to create this
circuit in hardware. They should be in the cardboard box of parts and stuff that
I left in the lab.

\begin{itemize}
  \item \texttt{TL082} \textsc{jfet}-input opamps (on breakout boards).
  \item A \textsc{vco} (voltage-controlled oscillator) part by \textsc{ti}.
  \item A \SI{4}{\MHz} crystal oscillator.
  \item A binary ripple-counter part (\textsc{cd}-series).
  \item Some \textsc{mux}es (maybe on breakout boards).
\end{itemize}

We just need to use opamps to differentiate $\tau(y)$ and then suitably offset
and scale that signal so that when $\dot{\tau} = \SI{0}{\s\per\s}$, the
input voltage to the \textsc{vco} will cause the \textsc{vco} to generate
a clock at $f_\textsc{rclk}$. Alternatively, make the differentiator inverting
and switch the role of \texttt{WCLK} and \textsc{RCLK}.

\end{document}

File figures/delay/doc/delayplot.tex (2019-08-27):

\documentclass[11pt,letterpaper]{article}

\usepackage{graphicx}
\usepackage{mathpazo}

\usepackage{minted}
\usemintedstyle{arduino}

\usepackage{geometry}
\geometry{margin=1in}

\title{Delay Plot GNUPlot Output and Code}
\author{Alex Striff}
\date{August 26, 2018}

\begin{document}
\maketitle

\begin{figure}[H]
  \centering
  \colorbox{white}{%
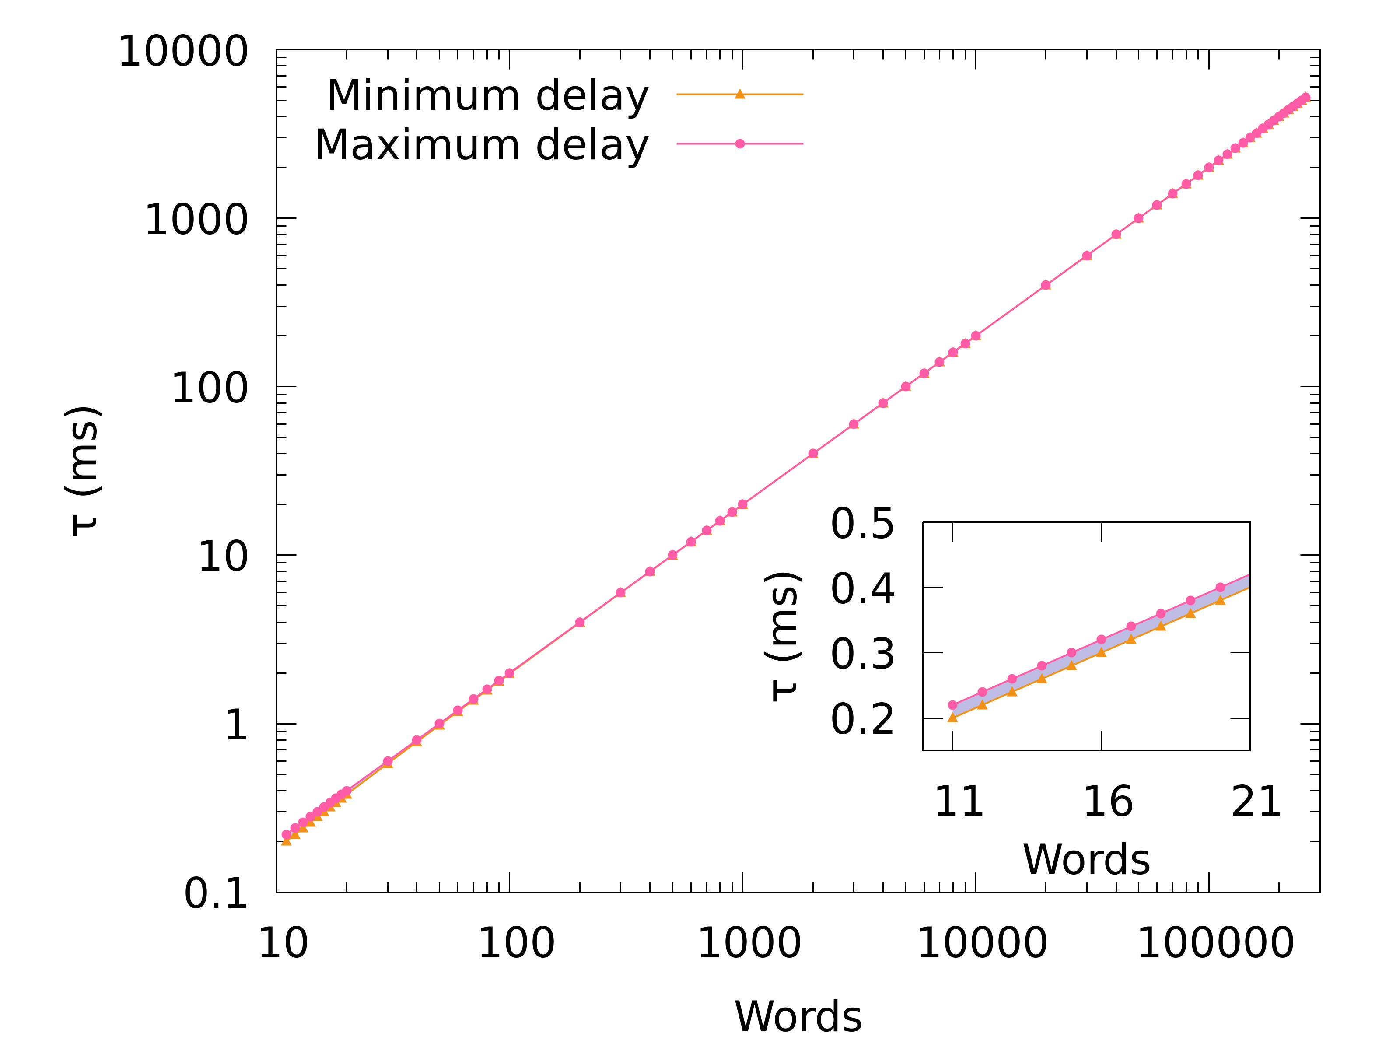
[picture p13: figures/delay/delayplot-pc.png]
    
  }
  \caption{Paper, color version.}
\end{figure}
\begin{figure}[H]
  \centering
  \colorbox{white}{%
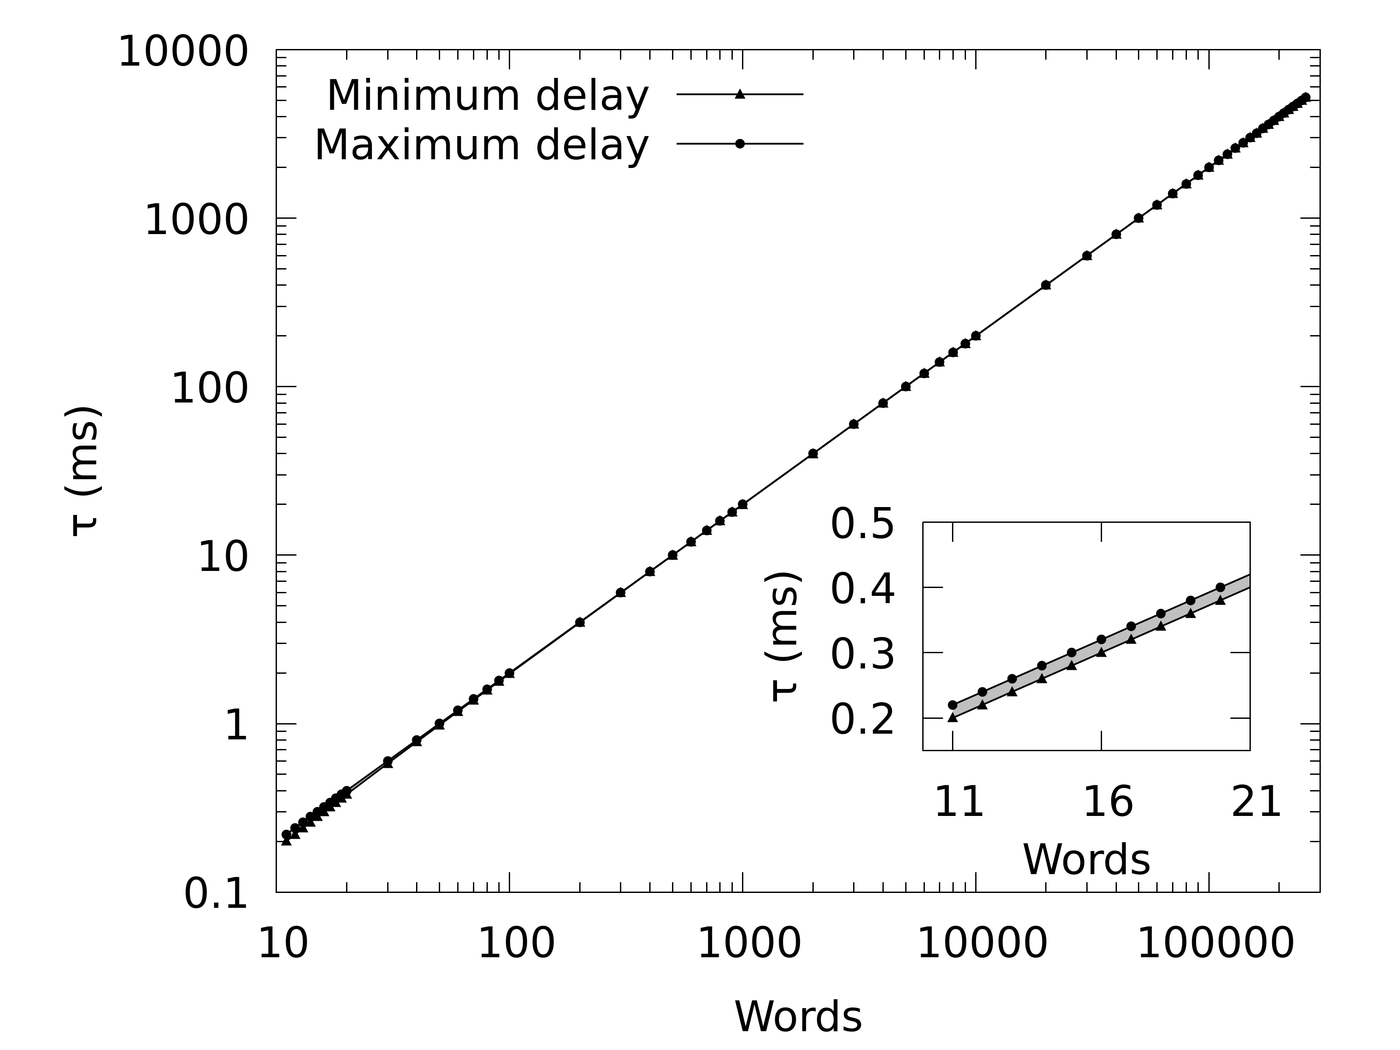
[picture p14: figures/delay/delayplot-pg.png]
    
  }
  \caption{Paper, grayscale version.}
\end{figure}
\begin{figure}[H]
  \centering
  \colorbox{black}{%
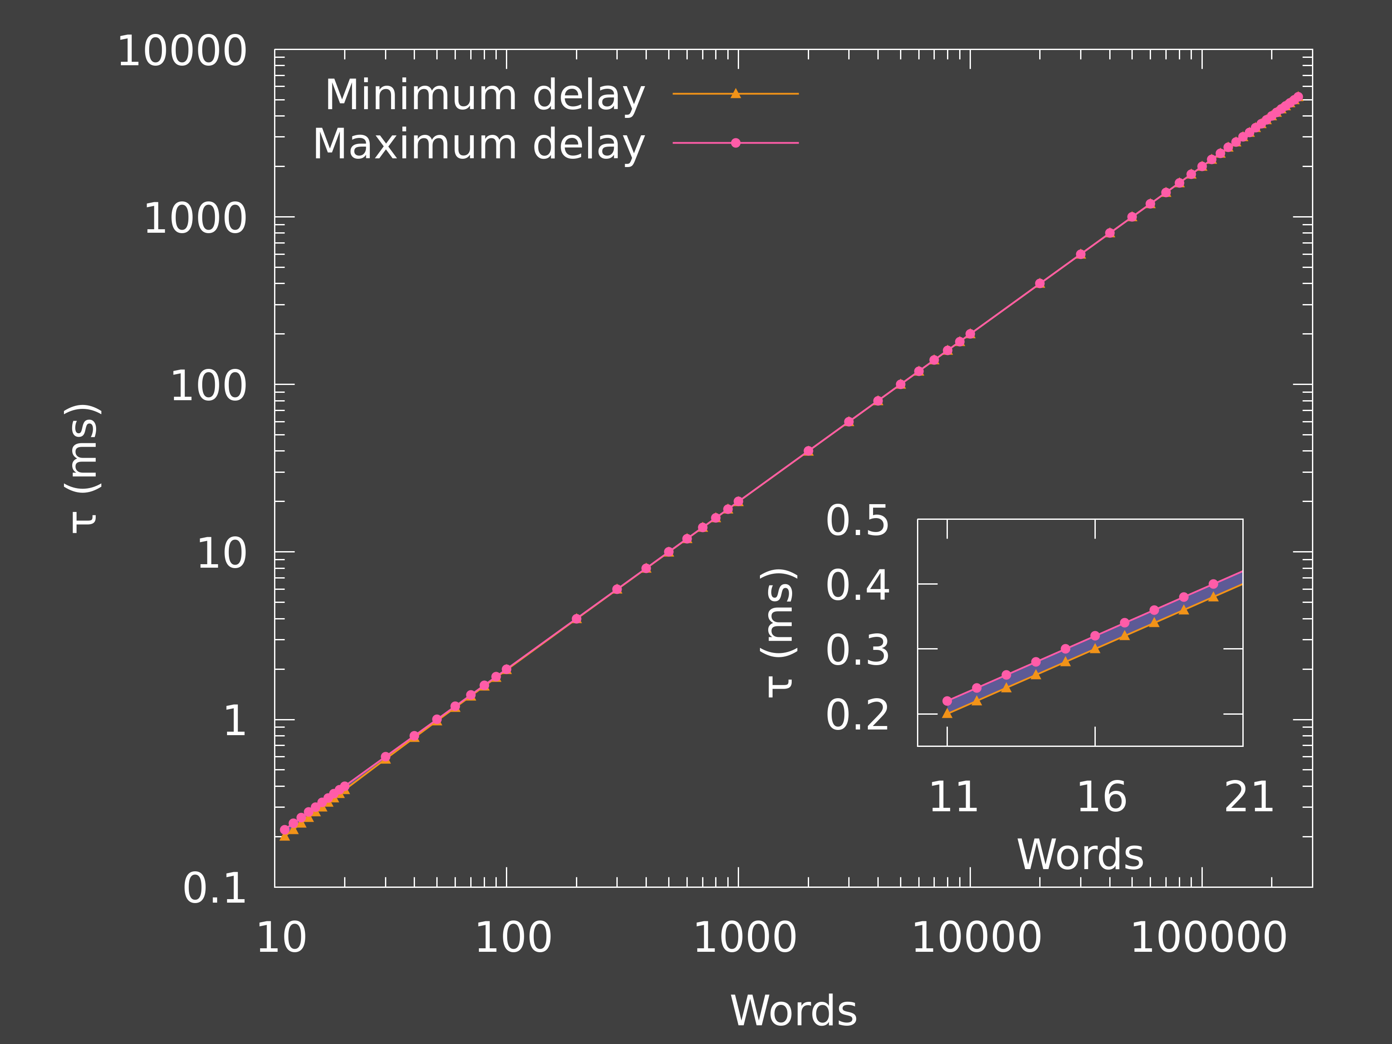
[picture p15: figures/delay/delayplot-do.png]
    
  }
  \caption{Dark Owl version (beamer slides).}
\end{figure}

\begin{minted}{gnuplot}
set terminal pngcairo transparent enhanced font "Droid Sans,72" \
      fontscale 1.0 size 3200, 2400

# Dark Owl
text = '#ffffff'
shade = '#5d5a96' # (rgb(OwlRed) .+ rgb(OwlBlue)) .* 3/8
mindelay = '#f29318' # OwlYellow
maxdelay = '#ff5ca8' # OwlRed
set output 'delayplot-do.png'

# Paper Color
# text = '#000000'
# shade = '#bfbce4' # 0.25*OwlRed + 0.25*OwlBlue + 0.5*white
# mindelay = '#f29318' # OwlYellow
# maxdelay = '#ff5ca8' # OwlRed
# set output 'delayplot-pc.png'

# Paper Grayscale
# text = '#000000'
# shade = '#c0c0c0'
# mindelay = '#000000'
# maxdelay = '#000000'
# set output 'delayplot-pg.png'

set multiplot
set style increment default

set border lw 3 lc rgb text
set key tc rgb text
set xlabel tc rgb text
set ylabel tc rgb text

set datafile separator ','
dlin = 'delayplot.csv'

set origin 0,0
set size  1,1
set xtics auto
set key left top autotitle columnhead
set xlabel 'Words'
set ylabel 'τ (ms)' offset 1.5,0
set logscale xy

plot [10:3e5][] \
       dlin u 3:2:1 w filledcurves lt rgb shade t '', \
       dlin u 3:1 w linespoints pt 9 ps 3 lw 4 lc rgb mindelay t '', \
       dlin u 3:2 w linespoints pt 7 ps 3 lw 4 lc rgb maxdelay t '', \
       NaN w linespoints pt 9 ps 3 lw 4 lc rgb mindelay t 'Minimum delay', \
       NaN w linespoints pt 7 ps 3 lw 4 lc rgb maxdelay t 'Maximum delay'

set origin 0.5,0.15
set size  0.45,0.4
set xtics 11, 5
set ytics 0.1
unset key
set xlabel 'Words' offset 0,0.325
set ylabel 'τ (ms)' offset 1.5,0
unset logscale

plot [10:21][0.15:0.5] \
       dlin u 3:2:1 w filledcurves lc rgb shade, \
       dlin u 3:1 w linespoints pt 9 ps 3 lw 4 lc rgb mindelay, \
       dlin u 3:2 w linespoints pt 7 ps 3 lw 4 lc rgb maxdelay

unset multiplot

\end{minted}

\end{document}

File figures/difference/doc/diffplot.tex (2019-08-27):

\documentclass[11pt,letterpaper]{article}

\usepackage{graphicx}
\usepackage{mathpazo}

\usepackage{minted}
\usemintedstyle{arduino}

\usepackage{geometry}
\geometry{margin=1in}

\title{Difference Plot GNUPlot Output and Code}
\author{Alex Striff}
\date{August 26, 2018}

\begin{document}
\maketitle

\begin{figure}[H]
  \centering
  \colorbox{white}{%
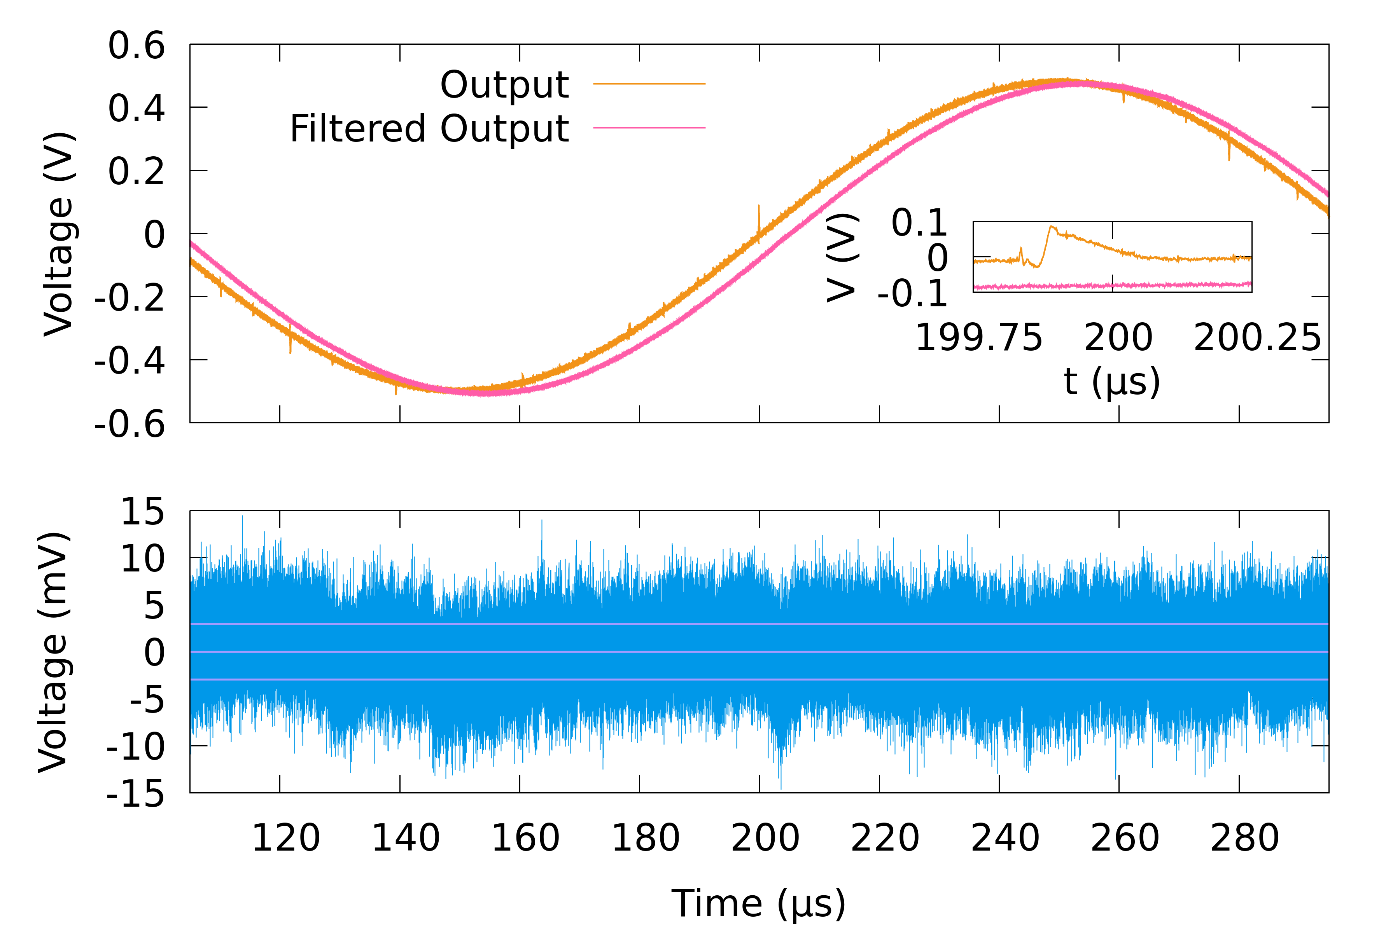
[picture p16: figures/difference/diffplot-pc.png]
    
  }
  \caption{Paper, color version.}
\end{figure}
\begin{figure}[H]
  \centering
  \colorbox{white}{%
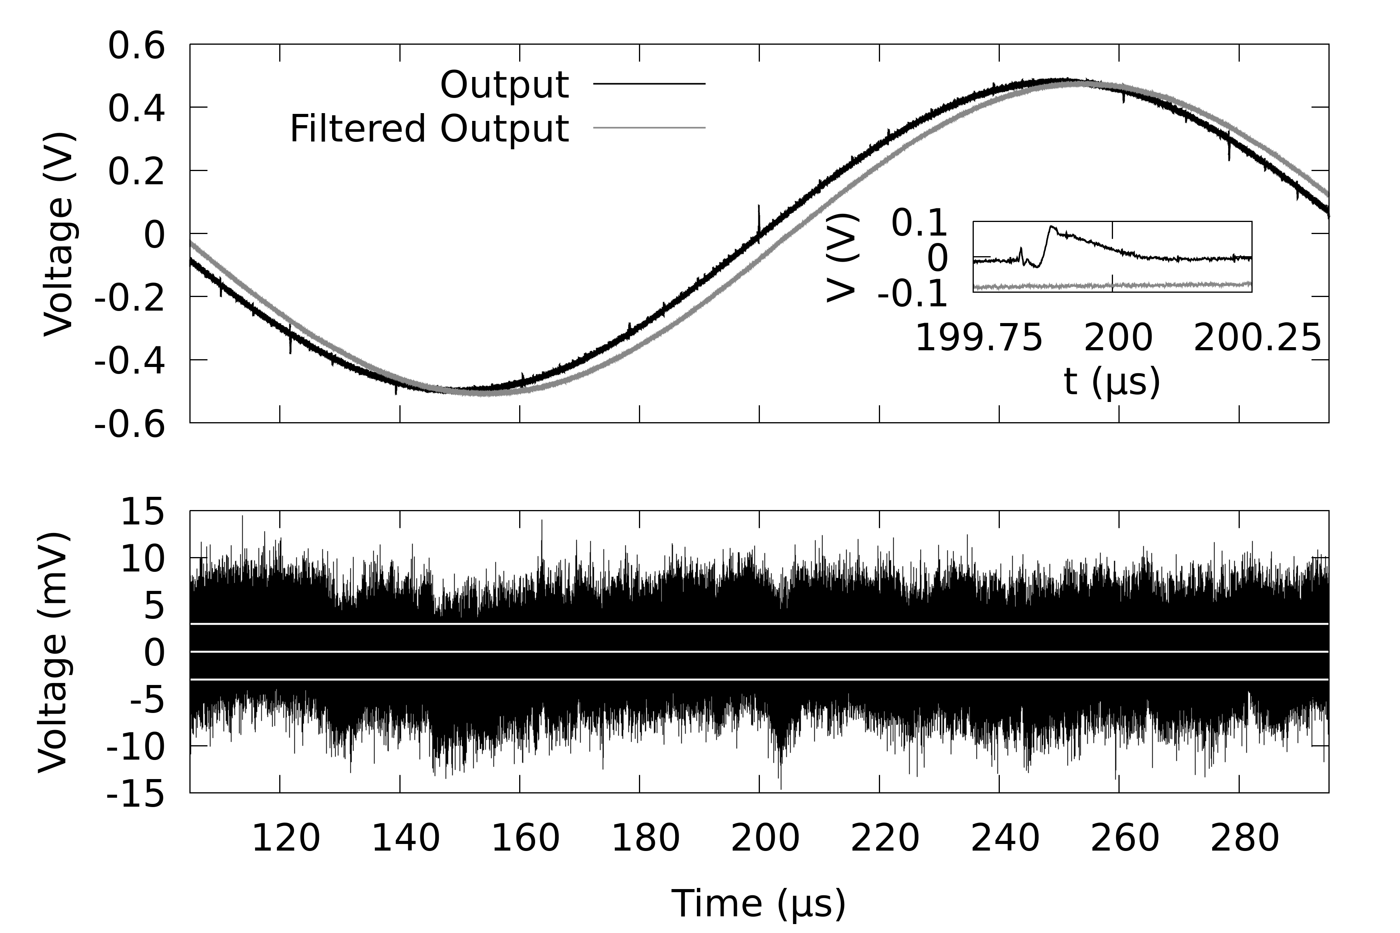
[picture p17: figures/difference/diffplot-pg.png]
    
  }
  \caption{Paper, grayscale version.}
\end{figure}
\begin{figure}[H]
  \centering
  \colorbox{black}{%
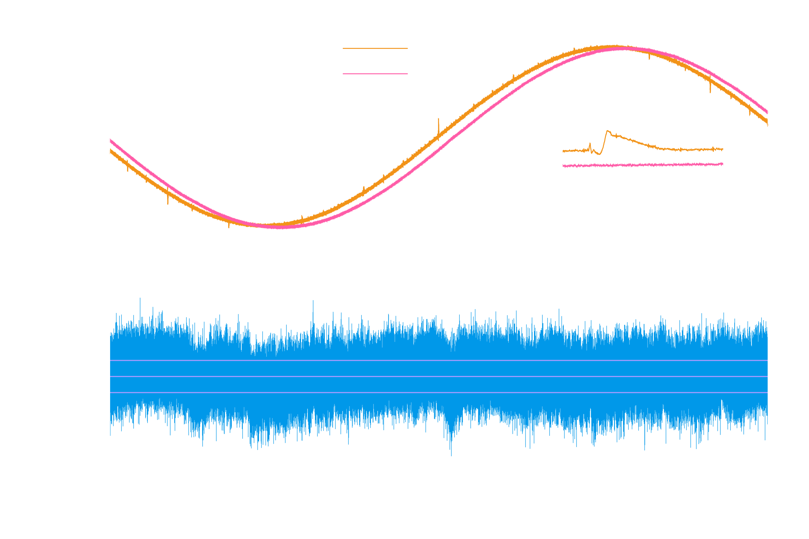
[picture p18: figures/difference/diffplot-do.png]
    
  }
  \caption{Dark Owl version (beamer slides).}
\end{figure}

\begin{minted}{gnuplot}
set terminal pngcairo transparent enhanced font "Droid Sans,72" \
      fontscale 1.0 size 3600, 2400

# Dark Owl
# text     = '#ffffff'
# aout     = '#f29318' # OwlYellow
# abessel4 = '#ff5ca8' # OwlRed
# adiff    = '#0098e9' # OwlBlue
# horiz    = '#a29bff' # (rgb(OwlRed) .+ rgb(OwlBlue)) norm. to max. blue
# set output 'diffplot-do.png'

# Paper Color
text     = '#000000'
aout     = '#f29318' # OwlYellow
abessel4 = '#ff5ca8' # OwlRed
adiff    = '#0098e9' # OwlBlue
horiz    = '#a29bff' # (rgb(OwlRed) .+ rgb(OwlBlue)) norm. to max. blue
set output 'diffplot-pc.png'

# Paper Grayscale
# text     = '#000000'
# aout     = '#000000'
# abessel4 = '#888888'
# adiff    = '#000000'
# horiz    = '#ffffff'
# set output 'diffplot-pg.png'

set border lw 3 lc rgb text
set key tc rgb text
set xlabel tc rgb text
set ylabel tc rgb text

set multiplot
set style increment default

set datafile separator ','
paout  = 'paout.csv'
padiff = 'padiff.csv'

# Difference
set size   1, 0.5
set origin 0, 0
set lmargin 8
set xtics auto
unset key
set xlabel 'Time (μs)'
set ylabel 'Voltage (mV)'
set xrange [105:295] noreverse writeback
# set xrange [199:201] noreverse writeback # Faster to plot for debugging

plot \
       padiff u 1:2 w lines lw 2 lt rgb adiff, \
       padiff u 1:3 w lines lw 5 lt rgb horiz, \
       padiff u 1:($3 + $4) w lines lw 5 lt rgb horiz, \
       padiff u 1:($3 - $4) w lines lw 5 lt rgb horiz

# Waveforms zoom-in
set size   0.25, 0.25
set origin 0.695, 0.56
set lmargin 0
set xtics auto 0.25
set ytics auto 0.1
unset key
set xlabel 't (μs)' offset 0,0.5
set ylabel 'V (V)' offset 1.25,0
set xrange [199.75:200.25] noreverse writeback

plot \
       paout u 3:($4 * 1e-3) w lines lw 4 lt rgb aout t '', \
       paout u 5:($6 * 1e-3) w lines lw 4 lt rgb abessel4 t ''

# Waveforms
set size   1, 0.5
set origin 0, 0.5
set lmargin 8
set xtics auto format ''
set ytics auto
unset xlabel
set key left top autotitle columnhead
set ylabel 'Voltage (V)'
set xrange [105:295] noreverse writeback
# set xrange [199:201] noreverse writeback # Faster to plot for debugging

plot \
       paout u 3:($4 * 1e-3) w lines lw 4 lt rgb aout t 'Output', \
       paout u 5:($6 * 1e-3) w lines lw 4 lt rgb abessel4 t 'Filtered Output'

unset multiplot

\end{minted}

\end{document}

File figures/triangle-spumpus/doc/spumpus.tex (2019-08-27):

\documentclass[11pt,letterpaper]{article}

\usepackage{graphicx}
\usepackage{mathpazo}

\usepackage{minted}
\usemintedstyle{arduino}

\usepackage{geometry}
\geometry{margin=1in}

\title{Triangle/Spumpus Plot GNUPlot Output and Code}
\author{Alex Striff}
\date{August 26, 2018}

\begin{document}
\maketitle

\begin{figure}[H]
  \centering
  \colorbox{white}{%
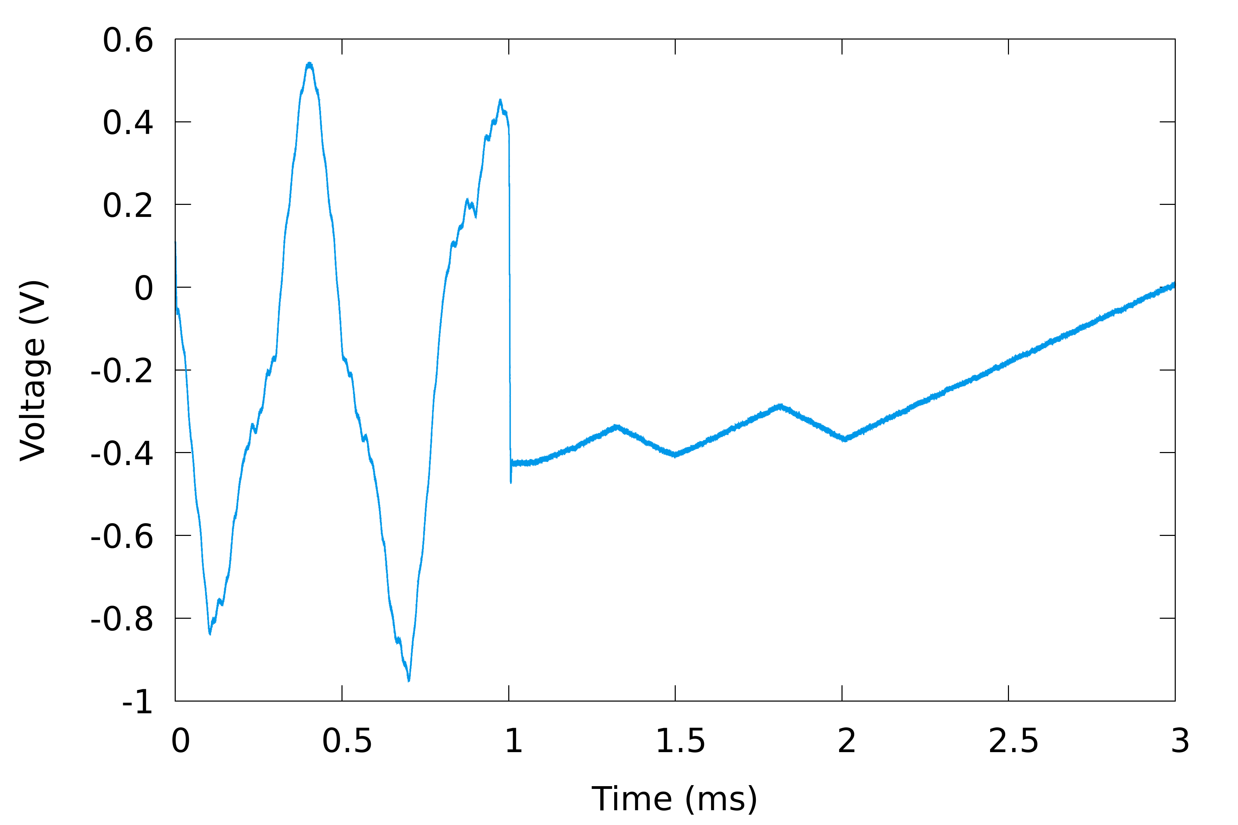
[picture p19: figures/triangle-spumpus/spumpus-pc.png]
    
  }
  \caption{Paper, color version.}
\end{figure}
\begin{figure}[H]
  \centering
  \colorbox{white}{%
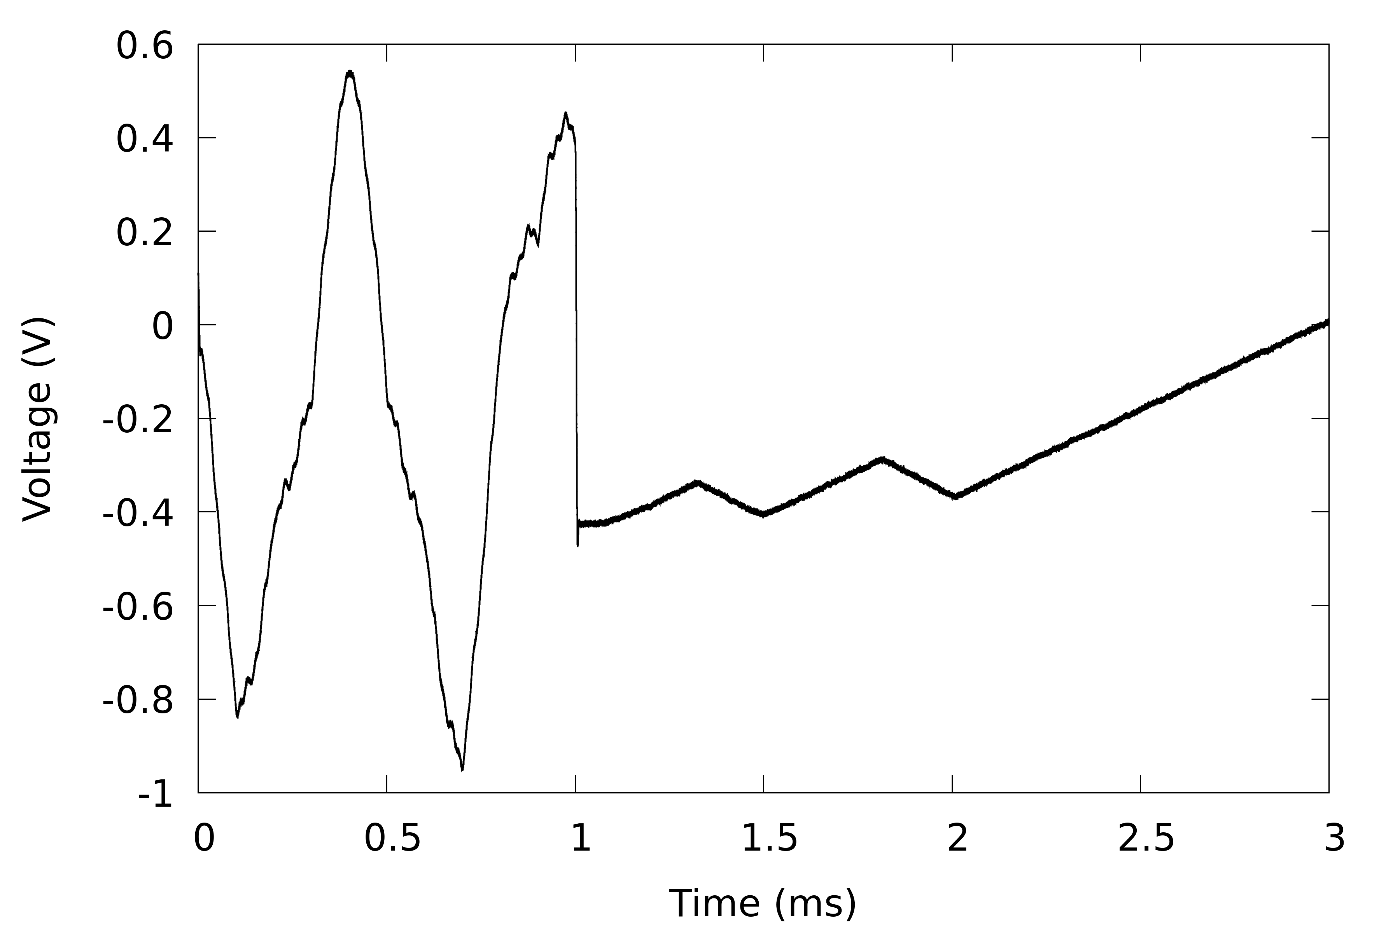
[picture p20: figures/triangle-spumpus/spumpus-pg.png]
    
  }
  \caption{Paper, grayscale version.}
\end{figure}
\begin{figure}[H]
  \centering
  \colorbox{black}{%
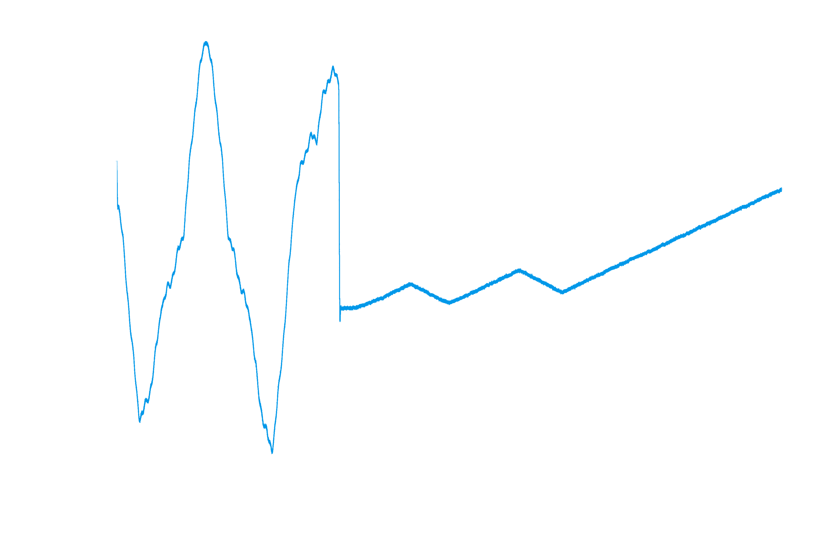
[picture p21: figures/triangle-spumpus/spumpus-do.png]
    
  }
  \caption{Dark Owl version (beamer slides).}
\end{figure}

\begin{minted}{gnuplot}
set terminal pngcairo transparent enhanced font "Droid Sans,72" \
      fontscale 1.0 size 3600, 2400

# Dark Owl
text = '#ffffff'
spcolor = '#0098e9' # OwlBlue
set output 'spumpus-do.png'

# Paper Color
# text = '#000000'
# spcolor = '#0098e9' # OwlBlue
# set output 'spumpus-pc.png'

# Paper Grayscale
# text = '#000000'
# spcolor = '#000000'
# set output 'spumpus-pg.png'

set style increment default

set border lw 3 lc rgb text
set xlabel tc rgb text
set ylabel tc rgb text

set datafile separator ','
sphist = 'spumpus-hist.csv'
spout  = 'spumpus-out.csv'

unset key
set xlabel 'Time (ms)'
set ylabel 'Voltage (V)'
set xrange [0:3] noreverse writeback

plot \
       sphist u ($1 * 1e3):($2) w lines lw 4 lt rgb spcolor

\end{minted}

\end{document}

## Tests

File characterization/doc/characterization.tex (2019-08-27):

% Default to the notebook output style

% Inherit from the specified cell style.

\documentclass[11pt]{article}

    \usepackage[T1]{fontenc}
    % Nicer default font (+ math font) than Computer Modern for most use cases
    \usepackage{mathpazo}

    % Basic figure setup, for now with no caption control since it's done
    % automatically by Pandoc (which extracts ![](path) syntax from Markdown).
    \usepackage{graphicx}
    % We will generate all images so they have a width \maxwidth. This means
    % that they will get their normal width if they fit onto the page, but
    % are scaled down if they would overflow the margins.
    \makeatletter
    \def\maxwidth{\ifdim\Gin@nat@width>\linewidth\linewidth
    \else\Gin@nat@width\fi}
    \makeatother
    \let\Oldincludegraphics\includegraphics
    % Set max figure width to be 80% of text width, for now hardcoded.
    \renewcommand{\includegraphics}[1]{\Oldincludegraphics[width=.8\maxwidth]{#1}}
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
\expandafter\def\csname PY@tok@kc\endcsname{\let\PY@bf=\textbf\def\PY@tc##1{\textcolor[rgb]{0.00,0.50,0.00}{##1}}}
\expandafter\def\csname PY@tok@kd\endcsname{\let\PY@bf=\textbf\def\PY@tc##1{\textcolor[rgb]{0.00,0.50,0.00}{##1}}}
\expandafter\def\csname PY@tok@kn\endcsname{\let\PY@bf=\textbf\def\PY@tc##1{\textcolor[rgb]{0.00,0.50,0.00}{##1}}}
\expandafter\def\csname PY@tok@kr\endcsname{\let\PY@bf=\textbf\def\PY@tc##1{\textcolor[rgb]{0.00,0.50,0.00}{##1}}}
\expandafter\def\csname PY@tok@bp\endcsname{\def\PY@tc##1{\textcolor[rgb]{0.00,0.50,0.00}{##1}}}
\expandafter\def\csname PY@tok@fm\endcsname{\def\PY@tc##1{\textcolor[rgb]{0.00,0.00,1.00}{##1}}}
\expandafter\def\csname PY@tok@vc\endcsname{\def\PY@tc##1{\textcolor[rgb]{0.10,0.09,0.49}{##1}}}
\expandafter\def\csname PY@tok@vg\endcsname{\def\PY@tc##1{\textcolor[rgb]{0.10,0.09,0.49}{##1}}}
\expandafter\def\csname PY@tok@vi\endcsname{\def\PY@tc##1{\textcolor[rgb]{0.10,0.09,0.49}{##1}}}
\expandafter\def\csname PY@tok@vm\endcsname{\def\PY@tc##1{\textcolor[rgb]{0.10,0.09,0.49}{##1}}}
\expandafter\def\csname PY@tok@sa\endcsname{\def\PY@tc##1{\textcolor[rgb]{0.73,0.13,0.13}{##1}}}
\expandafter\def\csname PY@tok@sb\endcsname{\def\PY@tc##1{\textcolor[rgb]{0.73,0.13,0.13}{##1}}}
\expandafter\def\csname PY@tok@sc\endcsname{\def\PY@tc##1{\textcolor[rgb]{0.73,0.13,0.13}{##1}}}
\expandafter\def\csname PY@tok@dl\endcsname{\def\PY@tc##1{\textcolor[rgb]{0.73,0.13,0.13}{##1}}}
\expandafter\def\csname PY@tok@s2\endcsname{\def\PY@tc##1{\textcolor[rgb]{0.73,0.13,0.13}{##1}}}
\expandafter\def\csname PY@tok@sh\endcsname{\def\PY@tc##1{\textcolor[rgb]{0.73,0.13,0.13}{##1}}}
\expandafter\def\csname PY@tok@s1\endcsname{\def\PY@tc##1{\textcolor[rgb]{0.73,0.13,0.13}{##1}}}
\expandafter\def\csname PY@tok@mb\endcsname{\def\PY@tc##1{\textcolor[rgb]{0.40,0.40,0.40}{##1}}}
\expandafter\def\csname PY@tok@mf\endcsname{\def\PY@tc##1{\textcolor[rgb]{0.40,0.40,0.40}{##1}}}
\expandafter\def\csname PY@tok@mh\endcsname{\def\PY@tc##1{\textcolor[rgb]{0.40,0.40,0.40}{##1}}}
\expandafter\def\csname PY@tok@mi\endcsname{\def\PY@tc##1{\textcolor[rgb]{0.40,0.40,0.40}{##1}}}
\expandafter\def\csname PY@tok@il\endcsname{\def\PY@tc##1{\textcolor[rgb]{0.40,0.40,0.40}{##1}}}
\expandafter\def\csname PY@tok@mo\endcsname{\def\PY@tc##1{\textcolor[rgb]{0.40,0.40,0.40}{##1}}}
\expandafter\def\csname PY@tok@ch\endcsname{\let\PY@it=\textit\def\PY@tc##1{\textcolor[rgb]{0.25,0.50,0.50}{##1}}}
\expandafter\def\csname PY@tok@cm\endcsname{\let\PY@it=\textit\def\PY@tc##1{\textcolor[rgb]{0.25,0.50,0.50}{##1}}}
\expandafter\def\csname PY@tok@cpf\endcsname{\let\PY@it=\textit\def\PY@tc##1{\textcolor[rgb]{0.25,0.50,0.50}{##1}}}
\expandafter\def\csname PY@tok@c1\endcsname{\let\PY@it=\textit\def\PY@tc##1{\textcolor[rgb]{0.25,0.50,0.50}{##1}}}
\expandafter\def\csname PY@tok@cs\endcsname{\let\PY@it=\textit\def\PY@tc##1{\textcolor[rgb]{0.25,0.50,0.50}{##1}}}

\def\PYZbs{\char`\\}
\def\PYZus{\char`\_}
\def\PYZob{\char`\{}
\def\PYZcb{\char`\}}
\def\PYZca{\char`\^}
\def\PYZam{\char`\&}
\def\PYZlt{\char`\<}
\def\PYZgt{\char`\>}
\def\PYZsh{\char`\#}
\def\PYZpc{\char`\%}
\def\PYZdl{\char`\$}
\def\PYZhy{\char`\-}
\def\PYZsq{\char`\'}
\def\PYZdq{\char`\"}
\def\PYZti{\char`\~}
% for compatibility with earlier versions
\def\PYZat{@}
\def\PYZlb{[}
\def\PYZrb{]}
\makeatother

    % Exact colors from NB
    \definecolor{incolor}{rgb}{0.0, 0.0, 0.5}
    \definecolor{outcolor}{rgb}{0.545, 0.0, 0.0}

    % Prevent overflowing lines due to hard-to-break entities
    \sloppy 
    % Setup hyperref package
    \hypersetup{
      breaklinks=true,  % so long urls are correctly broken across lines
      colorlinks=true,
      urlcolor=urlcolor,
      linkcolor=linkcolor,
      citecolor=citecolor,
      }
    % Slightly bigger margins than the latex defaults
    
    \geometry{verbose,tmargin=1in,bmargin=1in,lmargin=1in,rmargin=1in}

    \begin{document}

    \maketitle

    \begin{Verbatim}[commandchars=\\\{\}]
{\color{incolor}In [{\color{incolor}1}]:} \PY{k}{using} \PY{n}{StatsBase}
        \PY{k}{using} \PY{n}{Statistics}
        \PY{k}{using} \PY{n}{CSV}
        \PY{k}{using} \PY{n}{DSP}
        \PY{k}{using} \PY{n}{Measurements}
        \PY{k}{using} \PY{n}{CRC}
        \PY{k}{using} \PY{n}{Optim}
        \PY{k}{using} \PY{n}{Tables}
\end{Verbatim}

    \section{Delayed Signal Computations}\label{delayed-signal-computations}

    \subsection{DAC Rise Time}\label{dac-rise-time}

    \begin{Verbatim}[commandchars=\\\{\}]
{\color{incolor}In [{\color{incolor}2}]:} \PY{n}{rtdata} \PY{o}{=} \PY{n}{CSV}\PY{o}{.}\PY{n}{File}\PY{p}{(}\PY{l+s}{\PYZdq{}}\PY{l+s}{.}\PY{l+s}{/}\PY{l+s}{d}\PY{l+s}{a}\PY{l+s}{t}\PY{l+s}{a}\PY{l+s}{/}\PY{l+s}{T}\PY{l+s}{e}\PY{l+s}{k}\PY{l+s}{0}\PY{l+s}{0}\PY{l+s}{4}\PY{l+s}{.}\PY{l+s}{c}\PY{l+s}{s}\PY{l+s}{v}\PY{l+s}{\PYZdq{}}\PY{p}{;} \PY{n}{header}\PY{o}{=}\PY{k+kc}{false}\PY{p}{)}
        \PY{n}{rtweights} \PY{o}{=} \PY{n}{FrequencyWeights}\PY{p}{(}\PY{n}{rtdata}\PY{o}{.}\PY{n}{Column2}\PY{p}{)}
        \PY{n}{rt} \PY{o}{=} \PY{n}{mean}\PY{p}{(}\PY{n}{rtdata}\PY{o}{.}\PY{n}{Column1}\PY{p}{,} \PY{n}{rtweights}\PY{p}{)}
        \PY{n}{rtσ} \PY{o}{=} \PY{n}{std}\PY{p}{(}\PY{n}{rtdata}\PY{o}{.}\PY{n}{Column1}\PY{p}{,} \PY{n}{rtweights}\PY{p}{,} \PY{n}{corrected}\PY{o}{=}\PY{k+kc}{true}\PY{p}{)}
\end{Verbatim}

\begin{Verbatim}[commandchars=\\\{\}]
{\color{outcolor}Out[{\color{outcolor}2}]:} 1.1492676743389036e-9
\end{Verbatim}
            
    \begin{Verbatim}[commandchars=\\\{\}]
{\color{incolor}In [{\color{incolor}3}]:} \PY{n}{rtσ} \PY{o}{/=} \PY{l+m+mi}{4} \PY{c}{\PYZsh{} For a 1 Vpp square wave edge}
        \PY{n}{rt} \PY{o}{/=} \PY{l+m+mi}{4}
\end{Verbatim}

\begin{Verbatim}[commandchars=\\\{\}]
{\color{outcolor}Out[{\color{outcolor}3}]:} 1.290866506382043e-7
\end{Verbatim}
            
    \begin{Verbatim}[commandchars=\\\{\}]
{\color{incolor}In [{\color{incolor}4}]:} \PY{p}{(}\PY{n}{rt} \PY{n}{±} \PY{n}{rtσ}\PY{p}{)} \PY{o}{*} \PY{l+m+mf}{1e9}
\end{Verbatim}

\texttt{\color{outcolor}Out[{\color{outcolor}4}]:}
    
    $129.09 \pm 0.29$

    \subsection{Delay Error}\label{delay-error}

    The steps in the error plots are from single-digits on the scope, so the
results should taken with a grain of salt.

    \begin{Verbatim}[commandchars=\\\{\}]
{\color{incolor}In [{\color{incolor}5}]:} \PY{n}{dlimit}\PY{o}{=}\PY{l+m+mi}{35}\PY{p}{;}
        \PY{n}{ddata} \PY{o}{=} \PY{n}{CSV}\PY{o}{.}\PY{n}{File}\PY{p}{(}\PY{l+s}{\PYZdq{}}\PY{l+s}{.}\PY{l+s}{/}\PY{l+s}{d}\PY{l+s}{e}\PY{l+s}{l}\PY{l+s}{a}\PY{l+s}{y}\PY{l+s}{\PYZus{}}\PY{l+s}{l}\PY{l+s}{i}\PY{l+s}{n}\PY{l+s}{e}\PY{l+s}{a}\PY{l+s}{r}\PY{l+s}{i}\PY{l+s}{t}\PY{l+s}{y}\PY{l+s}{.}\PY{l+s}{c}\PY{l+s}{s}\PY{l+s}{v}\PY{l+s}{\PYZdq{}}\PY{p}{;} \PY{n}{skipto}\PY{o}{=}\PY{l+m+mi}{2}\PY{p}{,} \PY{n}{limit}\PY{o}{=}\PY{n}{dlimit}\PY{p}{,}
            \PY{n}{header}\PY{o}{=}\PY{p}{[}\PY{o}{:}\PY{n}{min}\PY{p}{,} \PY{o}{:}\PY{n}{max}\PY{p}{,} \PY{o}{:}\PY{n}{swords}\PY{p}{,} \PY{o}{:}\PY{n}{na}\PY{p}{,} \PY{o}{:}\PY{n}{clock}\PY{p}{,} \PY{o}{:}\PY{n}{signal}\PY{p}{,} \PY{o}{:}\PY{n}{rt}\PY{p}{]}\PY{p}{)}\PY{p}{;}
        \PY{n}{rtcorrection} \PY{o}{=} \PY{n}{vcat}\PY{p}{(}\PY{n}{repeat}\PY{p}{(}\PY{p}{[}\PY{n}{rt}\PY{p}{]}\PY{p}{,} \PY{l+m+mi}{13}\PY{p}{)}\PY{p}{,} \PY{n}{zeros}\PY{p}{(}\PY{n}{dlimit}\PY{o}{\PYZhy{}}\PY{l+m+mi}{13}\PY{p}{)}\PY{p}{)}\PY{p}{;}
        \PY{n}{minerr} \PY{o}{=} \PY{l+m+mf}{1e\PYZhy{}3}\PY{o}{.*}\PY{n}{ddata}\PY{o}{.}\PY{n}{min} \PY{o}{.\PYZhy{}} \PY{p}{(}\PY{n}{ddata}\PY{o}{.}\PY{n}{swords} \PY{o}{.*} \PY{l+m+mf}{20e\PYZhy{}6}\PY{p}{)} \PY{o}{.+} \PY{l+m+mf}{20e\PYZhy{}6} \PY{o}{\PYZhy{}} \PY{n}{rtcorrection}\PY{p}{;}
        \PY{n}{maxerr} \PY{o}{=} \PY{l+m+mf}{1e\PYZhy{}3}\PY{o}{.*}\PY{n}{ddata}\PY{o}{.}\PY{n}{max} \PY{o}{.\PYZhy{}} \PY{p}{(}\PY{n}{ddata}\PY{o}{.}\PY{n}{swords} \PY{o}{.*} \PY{l+m+mf}{20e\PYZhy{}6}\PY{p}{)} \PY{o}{\PYZhy{}} \PY{n}{rtcorrection}\PY{p}{;}
\end{Verbatim}

    \begin{Verbatim}[commandchars=\\\{\}]
{\color{incolor}In [{\color{incolor}6}]:} \PY{n}{last}\PY{p}{(}\PY{n}{ddata}\PY{o}{.}\PY{n}{swords}\PY{p}{)}
\end{Verbatim}

\begin{Verbatim}[commandchars=\\\{\}]
{\color{outcolor}Out[{\color{outcolor}6}]:} 9000
\end{Verbatim}
            
    Clock is at 50 kHz.

    \subsection{Estimated Internal Propagation
Delay}\label{estimated-internal-propagation-delay}

    Roughly estimated from risetime-corrected delay data.

    \begin{Verbatim}[commandchars=\\\{\}]
{\color{incolor}In [{\color{incolor}7}]:} \PY{n}{pt} \PY{o}{=} \PY{n}{mean}\PY{p}{(}\PY{n}{map}\PY{p}{(}\PY{n}{mean}\PY{p}{,} \PY{p}{[}\PY{n}{minerr}\PY{p}{[}\PY{l+m+mi}{1}\PY{o}{:}\PY{l+m+mi}{13}\PY{p}{]}\PY{p}{,} \PY{n}{maxerr}\PY{p}{[}\PY{l+m+mi}{1}\PY{o}{:}\PY{l+m+mi}{13}\PY{p}{]}\PY{p}{]}\PY{p}{)}\PY{p}{)} \PY{o}{./} \PY{l+m+mf}{1e\PYZhy{}9} \PY{c}{\PYZsh{} ns}
\end{Verbatim}

\begin{Verbatim}[commandchars=\\\{\}]
{\color{outcolor}Out[{\color{outcolor}7}]:} 40.14411859255405
\end{Verbatim}
            
    \subsection{In-Out Difference Mean}\label{in-out-difference-mean}

    \begin{Verbatim}[commandchars=\\\{\}]
{\color{incolor}In [{\color{incolor}8}]:} \PY{n}{meandata} \PY{o}{=} \PY{n}{CSV}\PY{o}{.}\PY{n}{File}\PY{p}{(}\PY{l+s}{\PYZdq{}}\PY{l+s}{.}\PY{l+s}{/}\PY{l+s}{d}\PY{l+s}{a}\PY{l+s}{t}\PY{l+s}{a}\PY{l+s}{/}\PY{l+s}{d}\PY{l+s}{i}\PY{l+s}{f}\PY{l+s}{f}\PY{l+s}{m}\PY{l+s}{e}\PY{l+s}{a}\PY{l+s}{n}\PY{l+s}{2}\PY{l+s}{.}\PY{l+s}{c}\PY{l+s}{s}\PY{l+s}{v}\PY{l+s}{\PYZdq{}}\PY{p}{;} \PY{n}{header}\PY{o}{=}\PY{k+kc}{false}\PY{p}{)}\PY{p}{;}
        \PY{n}{meanweights} \PY{o}{=} \PY{n}{FrequencyWeights}\PY{p}{(}\PY{n}{meandata}\PY{o}{.}\PY{n}{Column2}\PY{p}{)}\PY{p}{;}
        \PY{n}{diffμ} \PY{o}{=} \PY{n}{mean}\PY{p}{(}\PY{n}{meandata}\PY{o}{.}\PY{n}{Column1}\PY{p}{,} \PY{n}{meanweights}\PY{p}{)}\PY{p}{;}
        \PY{n}{diffμσ} \PY{o}{=} \PY{n}{std}\PY{p}{(}\PY{n}{meandata}\PY{o}{.}\PY{n}{Column1}\PY{p}{,} \PY{n}{meanweights}\PY{p}{,} \PY{n}{corrected}\PY{o}{=}\PY{k+kc}{true}\PY{p}{)}\PY{p}{;}
        \PY{p}{(}\PY{n}{diffμ} \PY{n}{±} \PY{n}{diffμσ}\PY{p}{)} \PY{o}{*} \PY{l+m+mf}{1e3} \PY{c}{\PYZsh{} mV}
\end{Verbatim}

\texttt{\color{outcolor}Out[{\color{outcolor}8}]:}
    
    $-1.023 \pm 0.095$

    \subsection{In-Out Difference ACRMS (Standard
Deviation)}\label{in-out-difference-acrms-standard-deviation}

    \begin{Verbatim}[commandchars=\\\{\}]
{\color{incolor}In [{\color{incolor}9}]:} \PY{n}{acrmsdata} \PY{o}{=} \PY{n}{CSV}\PY{o}{.}\PY{n}{File}\PY{p}{(}\PY{l+s}{\PYZdq{}}\PY{l+s}{.}\PY{l+s}{/}\PY{l+s}{d}\PY{l+s}{a}\PY{l+s}{t}\PY{l+s}{a}\PY{l+s}{/}\PY{l+s}{d}\PY{l+s}{i}\PY{l+s}{f}\PY{l+s}{f}\PY{l+s}{a}\PY{l+s}{c}\PY{l+s}{r}\PY{l+s}{m}\PY{l+s}{s}\PY{l+s}{2}\PY{l+s}{.}\PY{l+s}{c}\PY{l+s}{s}\PY{l+s}{v}\PY{l+s}{\PYZdq{}}\PY{p}{;} \PY{n}{header}\PY{o}{=}\PY{k+kc}{false}\PY{p}{)}\PY{p}{;}
        \PY{n}{acrmsweights} \PY{o}{=} \PY{n}{FrequencyWeights}\PY{p}{(}\PY{n}{acrmsdata}\PY{o}{.}\PY{n}{Column2}\PY{p}{)}\PY{p}{;}
        \PY{n}{diffσ} \PY{o}{=} \PY{n}{mean}\PY{p}{(}\PY{n}{acrmsdata}\PY{o}{.}\PY{n}{Column1}\PY{p}{,} \PY{n}{acrmsweights}\PY{p}{)}\PY{p}{;}
        \PY{n}{diffσσ} \PY{o}{=} \PY{n}{std}\PY{p}{(}\PY{n}{acrmsdata}\PY{o}{.}\PY{n}{Column1}\PY{p}{,} \PY{n}{acrmsweights}\PY{p}{,} \PY{n}{corrected}\PY{o}{=}\PY{k+kc}{true}\PY{p}{)}\PY{p}{;}
        \PY{p}{(}\PY{n}{diffσ} \PY{n}{±} \PY{n}{diffσσ}\PY{p}{)} \PY{o}{*} \PY{l+m+mf}{1e3} \PY{c}{\PYZsh{} mV (RMS)}
\end{Verbatim}

\texttt{\color{outcolor}Out[{\color{outcolor}9}]:}
    
    $1.035 \pm 0.058$

    \section{Output Plots}\label{output-plots}

    \begin{itemize}
\tightlist
\item
  Input: 50 Hz sine wave.
\item
  Clock: 50 kHz.
\item
  Delay: 1000 swords.
\item
  Measurement Bandwidth: 100 MHz.
\end{itemize}

    Ignore the naming of the file. The signal is actually at \emph{50 Hz}.

    \begin{Verbatim}[commandchars=\\\{\}]
{\color{incolor}In [{\color{incolor}10}]:} \PY{n}{diff500} \PY{o}{=} \PY{n}{CSV}\PY{o}{.}\PY{n}{File}\PY{p}{(}\PY{l+s}{\PYZdq{}}\PY{l+s}{.}\PY{l+s}{/}\PY{l+s}{d}\PY{l+s}{a}\PY{l+s}{t}\PY{l+s}{a}\PY{l+s}{/}\PY{l+s}{5}\PY{l+s}{0}\PY{l+s}{0}\PY{l+s}{H}\PY{l+s}{z}\PY{l+s}{D}\PY{l+s}{i}\PY{l+s}{f}\PY{l+s}{f}\PY{l+s}{1}\PY{l+s}{0}\PY{l+s}{0}\PY{l+s}{M}\PY{l+s}{H}\PY{l+s}{z}\PY{l+s}{.}\PY{l+s}{c}\PY{l+s}{s}\PY{l+s}{v}\PY{l+s}{\PYZdq{}}\PY{p}{,} \PY{n}{skipto}\PY{o}{=}\PY{l+m+mi}{10}\PY{p}{,} \PY{n}{header}\PY{o}{=}\PY{p}{[}\PY{o}{:}\PY{n}{t}\PY{p}{,} \PY{o}{:}\PY{n}{v}\PY{p}{]}\PY{p}{)}
\end{Verbatim}

\begin{Verbatim}[commandchars=\\\{\}]
{\color{outcolor}Out[{\color{outcolor}10}]:} CSV.File("./data/500HzDiff100MHz.csv"):
         Size: 1250000 x 2
         Tables.Schema:
          :t  Float64
          :v  Float64
\end{Verbatim}
            
    \begin{Verbatim}[commandchars=\\\{\}]
{\color{incolor}In [{\color{incolor}11}]:} \PY{c}{\PYZsh{} Resample/decimate for faster processing}
         \PY{c}{\PYZsh{}ddiff500t = resample(diff500.t, 1 // 10);}
         \PY{c}{\PYZsh{}ddiff500v = resample(diff500.v, 1 // 10);}
         
         \PY{n}{ddiff500t} \PY{o}{=} \PY{n}{diff500}\PY{o}{.}\PY{n}{t}\PY{p}{;}
         \PY{n}{ddiff500v} \PY{o}{=} \PY{n}{diff500}\PY{o}{.}\PY{n}{v}\PY{p}{;}
\end{Verbatim}

    \begin{itemize}
\tightlist
\item
  Input: 5 kHz sine wave.
\item
  Clock: 5 MHz.
\item
  Delay: 1000 swords.
\item
  Measurement Bandwidth: 250 MHz.
\end{itemize}

    Ignore the naming of the file. The signal is actually at \emph{5 kHz}.

    \begin{Verbatim}[commandchars=\\\{\}]
{\color{incolor}In [{\color{incolor}12}]:} \PY{n}{diff5M} \PY{o}{=} \PY{n}{CSV}\PY{o}{.}\PY{n}{File}\PY{p}{(}\PY{l+s}{\PYZdq{}}\PY{l+s}{.}\PY{l+s}{/}\PY{l+s}{d}\PY{l+s}{a}\PY{l+s}{t}\PY{l+s}{a}\PY{l+s}{/}\PY{l+s}{5}\PY{l+s}{M}\PY{l+s}{H}\PY{l+s}{z}\PY{l+s}{D}\PY{l+s}{i}\PY{l+s}{f}\PY{l+s}{f}\PY{l+s}{2}\PY{l+s}{5}\PY{l+s}{0}\PY{l+s}{M}\PY{l+s}{H}\PY{l+s}{z}\PY{l+s}{.}\PY{l+s}{c}\PY{l+s}{s}\PY{l+s}{v}\PY{l+s}{\PYZdq{}}\PY{p}{,} \PY{n}{skipto}\PY{o}{=}\PY{l+m+mi}{10}\PY{p}{,} \PY{n}{header}\PY{o}{=}\PY{p}{[}\PY{o}{:}\PY{n}{t}\PY{p}{,} \PY{o}{:}\PY{n}{v}\PY{p}{]}\PY{p}{)}
\end{Verbatim}

\begin{Verbatim}[commandchars=\\\{\}]
{\color{outcolor}Out[{\color{outcolor}12}]:} CSV.File("./data/5MHzDiff250MHz.csv"):
         Size: 625000 x 2
         Tables.Schema:
          :t  Float64
          :v  Float64
\end{Verbatim}
            
    \begin{Verbatim}[commandchars=\\\{\}]
{\color{incolor}In [{\color{incolor}13}]:} \PY{c}{\PYZsh{} Resample/decimate for faster processing}
         \PY{c}{\PYZsh{}ddiff5Mt = resample(diff5M.t, 1 // 10);}
         \PY{c}{\PYZsh{}ddiff5Mv = resample(diff5M.v, 1 // 10);}
         
         \PY{n}{ddiff5Mt} \PY{o}{=} \PY{n}{diff5M}\PY{o}{.}\PY{n}{t}\PY{p}{;}
         \PY{n}{ddiff5Mv} \PY{o}{=} \PY{n}{diff5M}\PY{o}{.}\PY{n}{v}\PY{p}{;}
\end{Verbatim}

    \section{Initial History Programming}\label{initial-history-programming}

    \begin{Verbatim}[commandchars=\\\{\}]
{\color{incolor}In [{\color{incolor}14}]:} \PY{n}{little\PYZus{}endian}\PY{p}{(}\PY{n}{x}\PY{p}{)} \PY{o}{=} \PY{k+kt}{UInt8}\PY{o}{.}\PY{p}{(}\PY{p}{[}\PY{n}{x} \PY{o}{\PYZam{}} \PY{l+m+mh}{0x00FF}\PY{p}{,} \PY{n}{x} \PY{o}{\PYZgt{}\PYZgt{}} \PY{l+m+mi}{8}\PY{p}{]}\PY{p}{)}\PY{p}{;}
\end{Verbatim}

    \begin{Verbatim}[commandchars=\\\{\}]
{\color{incolor}In [{\color{incolor}15}]:} \PY{n}{prog\PYZus{}words} \PY{o}{=} \PY{p}{[}
             \PY{l+m+mh}{0x0000}\PY{p}{,} \PY{l+m+mh}{0x07FF}\PY{p}{,} \PY{l+m+mh}{0x0FFF}\PY{p}{,} \PY{l+m+mh}{0x07FF}\PY{p}{,}
             \PY{l+m+mh}{0x0000}\PY{p}{,} \PY{l+m+mh}{0x07FF}\PY{p}{,} \PY{l+m+mh}{0x0FFF}\PY{p}{,} \PY{l+m+mh}{0x07FF}\PY{p}{,}
             \PY{l+m+mh}{0x0000}\PY{p}{,} \PY{l+m+mh}{0x07FF}\PY{p}{,} \PY{l+m+mh}{0x0FFF}\PY{p}{,} \PY{l+m+mh}{0x07FF}\PY{p}{,}
             \PY{l+m+mh}{0x0000}\PY{p}{,} \PY{l+m+mh}{0x07FF}\PY{p}{,} \PY{l+m+mh}{0x0FFF}\PY{p}{,} \PY{l+m+mh}{0x07FF}
         \PY{p}{]}\PY{p}{;}
         \PY{n}{waveform\PYZus{}file} \PY{o}{=} \PY{l+s}{\PYZdq{}}\PY{l+s}{.}\PY{l+s}{/}\PY{l+s}{p}\PY{l+s}{r}\PY{l+s}{o}\PY{l+s}{g}\PY{l+s}{\PYZus{}}\PY{l+s}{d}\PY{l+s}{e}\PY{l+s}{b}\PY{l+s}{u}\PY{l+s}{g}\PY{l+s}{.}\PY{l+s}{b}\PY{l+s}{i}\PY{l+s}{n}\PY{l+s}{\PYZdq{}}\PY{p}{;}
         \PY{n}{write}\PY{p}{(}\PY{n}{waveform\PYZus{}file}\PY{p}{,} \PY{n}{prog\PYZus{}words}\PY{p}{)}\PY{p}{;}
         \PY{n}{crc32} \PY{o}{=} \PY{n}{crc}\PY{p}{(}\PY{n}{CRC\PYZus{}32}\PY{p}{)}\PY{p}{;}
         \PY{n}{prog\PYZus{}crc} \PY{o}{=} \PY{n}{crc32}\PY{p}{(}\PY{n}{vcat}\PY{p}{(}\PY{n}{little\PYZus{}endian}\PY{o}{.}\PY{p}{(}\PY{n}{prog\PYZus{}words}\PY{p}{)}\PY{o}{.}\PY{o}{.}\PY{o}{.}\PY{p}{)}\PY{p}{)}\PY{p}{;}
         \PY{n}{display}\PY{p}{(}\PY{n}{prog\PYZus{}crc}\PY{p}{)}\PY{p}{;}
\end{Verbatim}

    \begin{verbatim}
0x7a569719
    \end{verbatim}

    \subsection{Initial History Programming
Instructions}\label{initial-history-programming-instructions}

    \begin{itemize}
\tightlist
\item
  Open \emph{Realterm}.
\item
  On the \emph{Display} tab, check the \emph{newLine mode} box.
\item
  On the \emph{Port} tab, set the \emph{Baud} rate to \emph{115200}.
\item
  Select the \emph{Port} that the \emph{Arduino Due} is plugged in to,
  such as \texttt{6\ =\ \textbackslash{}USBSER000}.
\item
  Press enter in the \emph{Port} field to open the port. You should see
  text from the Arduino Due.
\item
  On the \emph{Send} tab, select the first text field.
\item
  Type \texttt{ph\ N}, where \texttt{N} is the number of words that you
  want to program.
\item
  Click the \emph{Send ASCII} button. (Do not include a line feed in
  this command, as it will be interpreted as data).
\item
  In the \emph{Dump File to Port} section, click the ellipses
  (\texttt{...}) box.
\item
  Select the history data file that you want to program.
\item
  Under \emph{Delays}, set the first entry (\emph{Character Delay}) to
  \texttt{1}.
\item
  Click \emph{Send File}. You should see a hexdump of the data from the
  Arduino Due as it is transmitted.
\item
  At the end of the transmission, there will be a line that says
  \texttt{CRC:\ 0x...}. Check that this matches the \texttt{CRC\_32} of
  the sent data (little-endian).
\item
  Send the \texttt{go} command to the Arduino Due to switch to the
  external input and clocks.
\end{itemize}

    \section{Filtered Output Plots}\label{filtered-output-plots}

    \subsection{Signal A}\label{signal-a}

    \begin{itemize}
\tightlist
\item
  Input: 5 kHz sine wave.
\item
  Clock: 5 MHz.
\item
  Delay: 1000 swords.
\item
  Measurement Bandwidth: 250 MHz.
\end{itemize}

    \begin{Verbatim}[commandchars=\\\{\}]
{\color{incolor}In [{\color{incolor}16}]:} \PY{n}{ain} \PY{o}{=} \PY{n}{CSV}\PY{o}{.}\PY{n}{File}\PY{p}{(}\PY{l+s}{\PYZdq{}}\PY{l+s}{.}\PY{l+s}{/}\PY{l+s}{d}\PY{l+s}{a}\PY{l+s}{t}\PY{l+s}{a}\PY{l+s}{/}\PY{l+s}{5}\PY{l+s}{\PYZhy{}}\PY{l+s}{5}\PY{l+s}{\PYZhy{}}\PY{l+s}{i}\PY{l+s}{n}\PY{l+s}{.}\PY{l+s}{c}\PY{l+s}{s}\PY{l+s}{v}\PY{l+s}{\PYZdq{}}\PY{p}{,}
             \PY{n}{skipto}\PY{o}{=}\PY{l+m+mi}{10}\PY{p}{,} \PY{n}{header}\PY{o}{=}\PY{p}{[}\PY{o}{:}\PY{n}{t}\PY{p}{,} \PY{o}{:}\PY{n}{v}\PY{p}{]}\PY{p}{)}\PY{p}{;} \PY{c}{\PYZsh{} Input signal}
         \PY{n}{aout} \PY{o}{=} \PY{n}{CSV}\PY{o}{.}\PY{n}{File}\PY{p}{(}\PY{l+s}{\PYZdq{}}\PY{l+s}{.}\PY{l+s}{/}\PY{l+s}{d}\PY{l+s}{a}\PY{l+s}{t}\PY{l+s}{a}\PY{l+s}{/}\PY{l+s}{5}\PY{l+s}{\PYZhy{}}\PY{l+s}{5}\PY{l+s}{\PYZhy{}}\PY{l+s}{u}\PY{l+s}{n}\PY{l+s}{f}\PY{l+s}{i}\PY{l+s}{l}\PY{l+s}{t}\PY{l+s}{e}\PY{l+s}{r}\PY{l+s}{e}\PY{l+s}{d}\PY{l+s}{.}\PY{l+s}{c}\PY{l+s}{s}\PY{l+s}{v}\PY{l+s}{\PYZdq{}}\PY{p}{,}
             \PY{n}{skipto}\PY{o}{=}\PY{l+m+mi}{10}\PY{p}{,} \PY{n}{header}\PY{o}{=}\PY{p}{[}\PY{o}{:}\PY{n}{t}\PY{p}{,} \PY{o}{:}\PY{n}{v}\PY{p}{]}\PY{p}{)}\PY{p}{;} \PY{c}{\PYZsh{} Unfiltered output}
         \PY{n}{arc} \PY{o}{=} \PY{n}{CSV}\PY{o}{.}\PY{n}{File}\PY{p}{(}\PY{l+s}{\PYZdq{}}\PY{l+s}{.}\PY{l+s}{/}\PY{l+s}{d}\PY{l+s}{a}\PY{l+s}{t}\PY{l+s}{a}\PY{l+s}{/}\PY{l+s}{5}\PY{l+s}{\PYZhy{}}\PY{l+s}{5}\PY{l+s}{\PYZhy{}}\PY{l+s}{1}\PY{l+s}{0}\PY{l+s}{6}\PY{l+s}{k}\PY{l+s}{H}\PY{l+s}{z}\PY{l+s}{\PYZhy{}}\PY{l+s}{R}\PY{l+s}{C}\PY{l+s}{.}\PY{l+s}{c}\PY{l+s}{s}\PY{l+s}{v}\PY{l+s}{\PYZdq{}}\PY{p}{,}
             \PY{n}{skipto}\PY{o}{=}\PY{l+m+mi}{10}\PY{p}{,} \PY{n}{header}\PY{o}{=}\PY{p}{[}\PY{o}{:}\PY{n}{t}\PY{p}{,} \PY{o}{:}\PY{n}{v}\PY{p}{]}\PY{p}{)}\PY{p}{;} \PY{c}{\PYZsh{} 106 kHz RC filter (single\PYZhy{}pole)}
         \PY{n}{abessel4} \PY{o}{=} \PY{n}{CSV}\PY{o}{.}\PY{n}{File}\PY{p}{(}\PY{l+s}{\PYZdq{}}\PY{l+s}{.}\PY{l+s}{/}\PY{l+s}{d}\PY{l+s}{a}\PY{l+s}{t}\PY{l+s}{a}\PY{l+s}{/}\PY{l+s}{5}\PY{l+s}{\PYZhy{}}\PY{l+s}{5}\PY{l+s}{\PYZhy{}}\PY{l+s}{b}\PY{l+s}{e}\PY{l+s}{s}\PY{l+s}{s}\PY{l+s}{e}\PY{l+s}{l}\PY{l+s}{4}\PY{l+s}{.}\PY{l+s}{c}\PY{l+s}{s}\PY{l+s}{v}\PY{l+s}{\PYZdq{}}\PY{p}{,}
             \PY{n}{skipto}\PY{o}{=}\PY{l+m+mi}{10}\PY{p}{,} \PY{n}{header}\PY{o}{=}\PY{p}{[}\PY{o}{:}\PY{n}{t}\PY{p}{,} \PY{o}{:}\PY{n}{v}\PY{p}{]}\PY{p}{)}\PY{p}{;} \PY{c}{\PYZsh{} \PYZti{}121 kHz Bessel filter (four\PYZhy{}pole)}
\end{Verbatim}

    \begin{Verbatim}[commandchars=\\\{\}]
{\color{incolor}In [{\color{incolor}17}]:} \PY{n}{abessel4vpp} \PY{o}{=} \PY{n}{maximum}\PY{p}{(}\PY{n}{abessel4}\PY{o}{.}\PY{n}{v}\PY{p}{)} \PY{o}{\PYZhy{}} \PY{n}{minimum}\PY{p}{(}\PY{n}{abessel4}\PY{o}{.}\PY{n}{v}\PY{p}{)}\PY{p}{;}
\end{Verbatim}

    \subsection{Signal B}\label{signal-b}

    \begin{itemize}
\tightlist
\item
  Input: 20 kHz symmetric triangle wave.
\item
  Clock: 5 MHz.
\item
  Delay: 1000 swords.
\item
  Measurement Bandwidth: 250 MHz.
\end{itemize}
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

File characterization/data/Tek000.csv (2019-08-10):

2.11933e-06 | 0
2.12027e-06 | 0
2.12121e-06 | 0
2.12215e-06 | 0
2.12309e-06 | 0
2.12404e-06 | 0
2.12498e-06 | 0
2.12592e-06 | 0
2.12686e-06 | 0
2.1278e-06 | 0
2.12874e-06 | 0
2.12969e-06 | 0
2.13063e-06 | 0
2.13157e-06 | 0
2.13251e-06 | 0
2.13345e-06 | 0
2.13439e-06 | 0
2.13534e-06 | 0
2.13628e-06 | 0
2.13722e-06 | 0
2.13816e-06 | 0
2.1391e-06 | 0
2.14004e-06 | 0
2.14099e-06 | 0
2.14193e-06 | 0
2.14287e-06 | 0
2.14381e-06 | 0
2.14475e-06 | 0
2.14569e-06 | 0
2.14664e-06 | 0
2.14758e-06 | 0
2.14852e-06 | 0
2.14946e-06 | 0
2.1504e-06 | 0
2.15134e-06 | 0
2.15229e-06 | 0
2.15323e-06 | 0
2.15417e-06 | 0
2.15511e-06 | 0
2.15605e-06 | 0
2.15699e-06 | 0
2.15794e-06 | 0
2.15888e-06 | 0
2.15982e-06 | 0
2.16076e-06 | 0
2.1617e-06 | 0
2.16264e-06 | 0
2.16359e-06 | 0
2.16453e-06 | 0
2.16547e-06 | 0
2.16641e-06 | 0
2.16735e-06 | 0
2.16829e-06 | 0
2.16924e-06 | 0
2.17018e-06 | 0
2.17112e-06 | 0
2.17206e-06 | 0
2.173e-06 | 0
2.17394e-06 | 0
2.17489e-06 | 0
2.17583e-06 | 0
2.17677e-06 | 0
2.17771e-06 | 0
2.17865e-06 | 0
2.17959e-06 | 0
2.18054e-06 | 0
2.18148e-06 | 0
2.18242e-06 | 0
2.18336e-06 | 0
2.1843e-06 | 0
2.18524e-06 | 0
2.18619e-06 | 0
2.18713e-06 | 0
2.18807e-06 | 0
2.18901e-06 | 0
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

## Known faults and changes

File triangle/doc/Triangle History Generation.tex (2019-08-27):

% Default to the notebook output style

% Inherit from the specified cell style.

\documentclass[11pt]{article}

    \usepackage[T1]{fontenc}
    % Nicer default font (+ math font) than Computer Modern for most use cases
    \usepackage{mathpazo}

    % Basic figure setup, for now with no caption control since it's done
    % automatically by Pandoc (which extracts ![](path) syntax from Markdown).
    \usepackage{graphicx}
    % We will generate all images so they have a width \maxwidth. This means
    % that they will get their normal width if they fit onto the page, but
    % are scaled down if they would overflow the margins.
    \makeatletter
    \def\maxwidth{\ifdim\Gin@nat@width>\linewidth\linewidth
    \else\Gin@nat@width\fi}
    \makeatother
    \let\Oldincludegraphics\includegraphics
    % Set max figure width to be 80% of text width, for now hardcoded.
    \renewcommand{\includegraphics}[1]{\Oldincludegraphics[width=.8\maxwidth]{#1}}
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
\expandafter\def\csname PY@tok@kc\endcsname{\let\PY@bf=\textbf\def\PY@tc##1{\textcolor[rgb]{0.00,0.50,0.00}{##1}}}
\expandafter\def\csname PY@tok@kd\endcsname{\let\PY@bf=\textbf\def\PY@tc##1{\textcolor[rgb]{0.00,0.50,0.00}{##1}}}
\expandafter\def\csname PY@tok@kn\endcsname{\let\PY@bf=\textbf\def\PY@tc##1{\textcolor[rgb]{0.00,0.50,0.00}{##1}}}
\expandafter\def\csname PY@tok@kr\endcsname{\let\PY@bf=\textbf\def\PY@tc##1{\textcolor[rgb]{0.00,0.50,0.00}{##1}}}
\expandafter\def\csname PY@tok@bp\endcsname{\def\PY@tc##1{\textcolor[rgb]{0.00,0.50,0.00}{##1}}}
\expandafter\def\csname PY@tok@fm\endcsname{\def\PY@tc##1{\textcolor[rgb]{0.00,0.00,1.00}{##1}}}
\expandafter\def\csname PY@tok@vc\endcsname{\def\PY@tc##1{\textcolor[rgb]{0.10,0.09,0.49}{##1}}}
\expandafter\def\csname PY@tok@vg\endcsname{\def\PY@tc##1{\textcolor[rgb]{0.10,0.09,0.49}{##1}}}
\expandafter\def\csname PY@tok@vi\endcsname{\def\PY@tc##1{\textcolor[rgb]{0.10,0.09,0.49}{##1}}}
\expandafter\def\csname PY@tok@vm\endcsname{\def\PY@tc##1{\textcolor[rgb]{0.10,0.09,0.49}{##1}}}
\expandafter\def\csname PY@tok@sa\endcsname{\def\PY@tc##1{\textcolor[rgb]{0.73,0.13,0.13}{##1}}}
\expandafter\def\csname PY@tok@sb\endcsname{\def\PY@tc##1{\textcolor[rgb]{0.73,0.13,0.13}{##1}}}
\expandafter\def\csname PY@tok@sc\endcsname{\def\PY@tc##1{\textcolor[rgb]{0.73,0.13,0.13}{##1}}}
\expandafter\def\csname PY@tok@dl\endcsname{\def\PY@tc##1{\textcolor[rgb]{0.73,0.13,0.13}{##1}}}
\expandafter\def\csname PY@tok@s2\endcsname{\def\PY@tc##1{\textcolor[rgb]{0.73,0.13,0.13}{##1}}}
\expandafter\def\csname PY@tok@sh\endcsname{\def\PY@tc##1{\textcolor[rgb]{0.73,0.13,0.13}{##1}}}
\expandafter\def\csname PY@tok@s1\endcsname{\def\PY@tc##1{\textcolor[rgb]{0.73,0.13,0.13}{##1}}}
\expandafter\def\csname PY@tok@mb\endcsname{\def\PY@tc##1{\textcolor[rgb]{0.40,0.40,0.40}{##1}}}
\expandafter\def\csname PY@tok@mf\endcsname{\def\PY@tc##1{\textcolor[rgb]{0.40,0.40,0.40}{##1}}}
\expandafter\def\csname PY@tok@mh\endcsname{\def\PY@tc##1{\textcolor[rgb]{0.40,0.40,0.40}{##1}}}
\expandafter\def\csname PY@tok@mi\endcsname{\def\PY@tc##1{\textcolor[rgb]{0.40,0.40,0.40}{##1}}}
\expandafter\def\csname PY@tok@il\endcsname{\def\PY@tc##1{\textcolor[rgb]{0.40,0.40,0.40}{##1}}}
\expandafter\def\csname PY@tok@mo\endcsname{\def\PY@tc##1{\textcolor[rgb]{0.40,0.40,0.40}{##1}}}
\expandafter\def\csname PY@tok@ch\endcsname{\let\PY@it=\textit\def\PY@tc##1{\textcolor[rgb]{0.25,0.50,0.50}{##1}}}
\expandafter\def\csname PY@tok@cm\endcsname{\let\PY@it=\textit\def\PY@tc##1{\textcolor[rgb]{0.25,0.50,0.50}{##1}}}
\expandafter\def\csname PY@tok@cpf\endcsname{\let\PY@it=\textit\def\PY@tc##1{\textcolor[rgb]{0.25,0.50,0.50}{##1}}}
\expandafter\def\csname PY@tok@c1\endcsname{\let\PY@it=\textit\def\PY@tc##1{\textcolor[rgb]{0.25,0.50,0.50}{##1}}}
\expandafter\def\csname PY@tok@cs\endcsname{\let\PY@it=\textit\def\PY@tc##1{\textcolor[rgb]{0.25,0.50,0.50}{##1}}}

\def\PYZbs{\char`\\}
\def\PYZus{\char`\_}
\def\PYZob{\char`\{}
\def\PYZcb{\char`\}}
\def\PYZca{\char`\^}
\def\PYZam{\char`\&}
\def\PYZlt{\char`\<}
\def\PYZgt{\char`\>}
\def\PYZsh{\char`\#}
\def\PYZpc{\char`\%}
\def\PYZdl{\char`\$}
\def\PYZhy{\char`\-}
\def\PYZsq{\char`\'}
\def\PYZdq{\char`\"}
\def\PYZti{\char`\~}
% for compatibility with earlier versions
\def\PYZat{@}
\def\PYZlb{[}
\def\PYZrb{]}
\makeatother

    % Exact colors from NB
    \definecolor{incolor}{rgb}{0.0, 0.0, 0.5}
    \definecolor{outcolor}{rgb}{0.545, 0.0, 0.0}

    % Prevent overflowing lines due to hard-to-break entities
    \sloppy 
    % Setup hyperref package
    \hypersetup{
      breaklinks=true,  % so long urls are correctly broken across lines
      colorlinks=true,
      urlcolor=urlcolor,
      linkcolor=linkcolor,
      citecolor=citecolor,
      }
    % Slightly bigger margins than the latex defaults
    
    \geometry{verbose,tmargin=1in,bmargin=1in,lmargin=1in,rmargin=1in}

    \begin{document}

    \maketitle

    \begin{Verbatim}[commandchars=\\\{\}]
{\color{incolor}In [{\color{incolor}1}]:} \PY{k}{using} \PY{n}{CRC}
        \PY{k}{using} \PY{n}{Plots}
        
        \PY{n}{gr}\PY{p}{(}\PY{p}{)}
\end{Verbatim}

\begin{Verbatim}[commandchars=\\\{\}]
{\color{outcolor}Out[{\color{outcolor}1}]:} Plots.GRBackend()
\end{Verbatim}
            
    \begin{Verbatim}[commandchars=\\\{\}]
{\color{incolor}In [{\color{incolor}2}]:} \PY{n}{f} \PY{o}{=} \PY{l+m+mf}{6e6}\PY{p}{;}
        \PY{n}{τ} \PY{o}{=} \PY{l+m+mf}{1e\PYZhy{}3}\PY{p}{;}
        \PY{n}{n} \PY{o}{=} \PY{n}{τ}\PY{o}{*}\PY{n}{f}\PY{p}{;}
\end{Verbatim}

    The last two words will be replaced with a value close to 0V (0x0800)
when programmed, since we cannot program the initial DAC output.

    \begin{Verbatim}[commandchars=\\\{\}]
{\color{incolor}In [{\color{incolor}3}]:} \PY{n}{g}\PY{p}{(}\PY{n}{t}\PY{p}{)} \PY{o}{=} \PY{o}{\PYZhy{}}\PY{l+m+mf}{0.45} \PY{o}{*} \PY{p}{(}\PY{l+m+mf}{0.9} \PY{o}{*} \PY{n}{sin}\PY{p}{(}\PY{n}{t} \PY{o}{*} \PY{l+m+mf}{2.5}\PY{o}{*}\PY{l+m+mi}{3}\PY{n+nb}{π} \PY{o}{/} \PY{l+m+mi}{2}\PY{p}{)} \PY{o}{*} \PY{n}{atan}\PY{p}{(}\PY{l+m+mi}{8}\PY{n+nb}{π} \PY{o}{*} \PY{n}{t}\PY{p}{)}
            \PY{o}{\PYZhy{}} \PY{l+m+mf}{0.1} \PY{o}{*} \PY{n}{abs}\PY{p}{(}\PY{n}{atan}\PY{p}{(}\PY{n}{sec}\PY{p}{(}\PY{n}{t} \PY{o}{*} \PY{l+m+mi}{20}\PY{n+nb}{π}\PY{p}{)}\PY{p}{)}\PY{p}{)} \PY{o}{\PYZhy{}} \PY{l+m+mf}{0.5} \PY{o}{*} \PY{n}{abs}\PY{p}{(}\PY{n}{atan}\PY{p}{(}\PY{n}{cot}\PY{p}{(}\PY{n}{t} \PY{o}{*} \PY{l+m+mi}{5}\PY{n+nb}{π}\PY{p}{)}\PY{p}{)}\PY{p}{)}
            \PY{o}{+} \PY{l+m+mf}{0.02} \PY{o}{*} \PY{n}{cos}\PY{p}{(}\PY{l+m+mi}{100}\PY{n+nb}{π} \PY{o}{*} \PY{n}{t}\PY{p}{)}\PY{p}{)} \PY{o}{\PYZhy{}} \PY{l+m+mf}{0.4}\PY{p}{;}
        \PY{n}{ts} \PY{o}{=} \PY{p}{(}\PY{l+m+mi}{0}\PY{o}{:}\PY{n}{n}\PY{o}{\PYZhy{}}\PY{l+m+mi}{1}\PY{p}{)} \PY{o}{/} \PY{p}{(}\PY{n}{n}\PY{o}{\PYZhy{}}\PY{l+m+mi}{1}\PY{p}{)}\PY{p}{;}
        \PY{n}{gs} \PY{o}{=} \PY{n}{g}\PY{o}{.}\PY{p}{(}\PY{n}{ts}\PY{p}{)}\PY{p}{;}
        \PY{n}{plot}\PY{p}{(}\PY{n}{ts}\PY{p}{,} \PY{n}{gs}\PY{p}{,} \PY{n}{xlim}\PY{o}{=}\PY{p}{(}\PY{l+m+mi}{0}\PY{p}{,} \PY{l+m+mi}{1}\PY{p}{)}\PY{p}{,}
            \PY{n}{xlabel} \PY{o}{=} \PY{l+s}{\PYZdq{}}\PY{l+s}{N}\PY{l+s}{o}\PY{l+s}{n}\PY{l+s}{d}\PY{l+s}{i}\PY{l+s}{m}\PY{l+s}{e}\PY{l+s}{n}\PY{l+s}{s}\PY{l+s}{i}\PY{l+s}{o}\PY{l+s}{n}\PY{l+s}{a}\PY{l+s}{l}\PY{l+s}{i}\PY{l+s}{z}\PY{l+s}{e}\PY{l+s}{d}\PY{l+s}{ }\PY{l+s}{d}\PY{l+s}{e}\PY{l+s}{l}\PY{l+s}{a}\PY{l+s}{y}\PY{l+s}{ }\PY{l+s}{t}\PY{l+s}{i}\PY{l+s}{m}\PY{l+s}{e}\PY{l+s}{\PYZdq{}}\PY{p}{,}
            \PY{n}{ylabel} \PY{o}{=} \PY{l+s}{\PYZdq{}}\PY{l+s}{N}\PY{l+s}{o}\PY{l+s}{n}\PY{l+s}{d}\PY{l+s}{i}\PY{l+s}{m}\PY{l+s}{e}\PY{l+s}{n}\PY{l+s}{s}\PY{l+s}{i}\PY{l+s}{o}\PY{l+s}{n}\PY{l+s}{a}\PY{l+s}{l}\PY{l+s}{i}\PY{l+s}{z}\PY{l+s}{e}\PY{l+s}{d}\PY{l+s}{ }\PY{l+s}{a}\PY{l+s}{m}\PY{l+s}{p}\PY{l+s}{l}\PY{l+s}{i}\PY{l+s}{t}\PY{l+s}{u}\PY{l+s}{d}\PY{l+s}{e}\PY{l+s}{ }\PY{l+s}{(}\PY{l+s}{±}\PY{l+s}{1}\PY{l+s}{)}\PY{l+s}{\PYZdq{}}\PY{p}{,}
            \PY{n}{label} \PY{o}{=} \PY{l+s}{\PYZdq{}}\PY{l+s}{H}\PY{l+s}{i}\PY{l+s}{s}\PY{l+s}{t}\PY{l+s}{o}\PY{l+s}{r}\PY{l+s}{y}\PY{l+s}{ }\PY{l+s}{S}\PY{l+s}{i}\PY{l+s}{g}\PY{l+s}{n}\PY{l+s}{a}\PY{l+s}{l}\PY{l+s}{\PYZdq{}}\PY{p}{,} \PY{n}{legend}\PY{o}{=}\PY{o}{:}\PY{n}{topleft}\PY{p}{)}
\end{Verbatim}

\texttt{\color{outcolor}Out[{\color{outcolor}3}]:}
    
    \begin{center}
    \adjustimage{max size={0.9\linewidth}{0.9\paperheight}}{output_3_0.pdf}
    \end{center}
    { \hspace*{\fill} \\}

    \begin{Verbatim}[commandchars=\\\{\}]
{\color{incolor}In [{\color{incolor}4}]:} \PY{n}{little\PYZus{}endian}\PY{p}{(}\PY{n}{x}\PY{p}{)} \PY{o}{=} \PY{k+kt}{UInt8}\PY{o}{.}\PY{p}{(}\PY{p}{[}\PY{n}{x} \PY{o}{\PYZam{}} \PY{l+m+mh}{0x00FF}\PY{p}{,} \PY{n}{x} \PY{o}{\PYZgt{}\PYZgt{}} \PY{l+m+mi}{8}\PY{p}{]}\PY{p}{)}\PY{p}{;}
\end{Verbatim}

    \begin{Verbatim}[commandchars=\\\{\}]
{\color{incolor}In [{\color{incolor}5}]:} \PY{n}{prog\PYZus{}words} \PY{o}{=} \PY{k+kt}{UInt16}\PY{o}{.}\PY{p}{(}\PY{n}{round}\PY{o}{.}\PY{p}{(}\PY{l+m+mi}{2}\PY{o}{\PYZca{}}\PY{p}{(}\PY{l+m+mi}{12} \PY{o}{\PYZhy{}} \PY{l+m+mi}{1}\PY{p}{)} \PY{o}{*} \PY{p}{(}\PY{l+m+mi}{1} \PY{o}{.+} \PY{n}{gs}\PY{p}{)}\PY{p}{)}\PY{p}{)} \PY{o}{.}\PY{o}{\PYZam{}} \PY{l+m+mh}{0x0FFF}\PY{p}{;}
        \PY{n}{waveform\PYZus{}file} \PY{o}{=} \PY{l+s}{\PYZdq{}}\PY{l+s}{.}\PY{l+s}{/}\PY{l+s}{t}\PY{l+s}{r}\PY{l+s}{i}\PY{l+s}{a}\PY{l+s}{n}\PY{l+s}{g}\PY{l+s}{l}\PY{l+s}{e}\PY{l+s}{\PYZus{}}\PY{l+s}{h}\PY{l+s}{i}\PY{l+s}{s}\PY{l+s}{t}\PY{l+s}{.}\PY{l+s}{b}\PY{l+s}{i}\PY{l+s}{n}\PY{l+s}{\PYZdq{}}\PY{p}{;}
        \PY{n}{write}\PY{p}{(}\PY{n}{waveform\PYZus{}file}\PY{p}{,} \PY{n}{prog\PYZus{}words}\PY{p}{)}
\end{Verbatim}

\begin{Verbatim}[commandchars=\\\{\}]
{\color{outcolor}Out[{\color{outcolor}5}]:} 12000
\end{Verbatim}
            
    \begin{Verbatim}[commandchars=\\\{\}]
{\color{incolor}In [{\color{incolor}6}]:} \PY{n}{crc32} \PY{o}{=} \PY{n}{crc}\PY{p}{(}\PY{n}{CRC\PYZus{}32}\PY{p}{)}\PY{p}{;}
        \PY{n}{prog\PYZus{}crc} \PY{o}{=} \PY{n}{crc32}\PY{p}{(}\PY{n}{vcat}\PY{p}{(}\PY{n}{little\PYZus{}endian}\PY{o}{.}\PY{p}{(}\PY{n}{prog\PYZus{}words}\PY{p}{)}\PY{o}{.}\PY{o}{.}\PY{o}{.}\PY{p}{)}\PY{p}{)}
\end{Verbatim}

\begin{Verbatim}[commandchars=\\\{\}]
{\color{outcolor}Out[{\color{outcolor}6}]:} 0x701bff42
\end{Verbatim}

    % Add a bibliography block to the postdoc

    \end{document}

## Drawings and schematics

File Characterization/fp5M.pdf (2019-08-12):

## 250.0 kHz filters on 5 MHz clock difference data

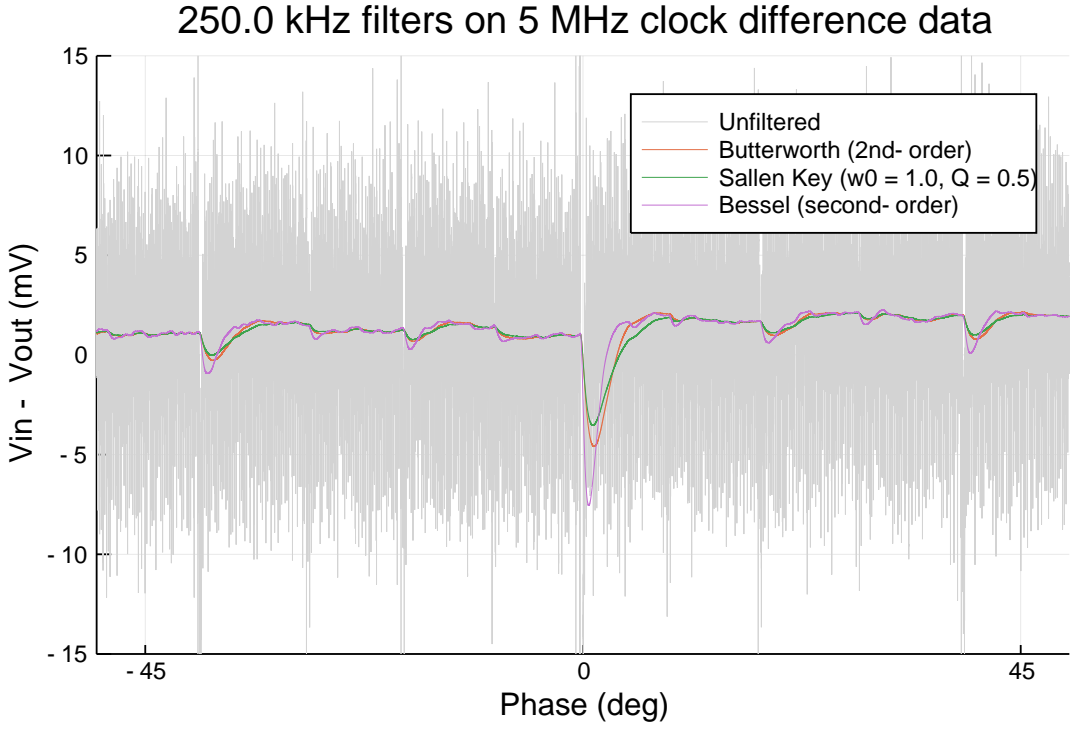
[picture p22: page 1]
Phase (deg)

Unfiltered
Butterworth (2nd-order)
Sallen Key (w0 = 1.0, Q = 0.5)
Bessel (second-order)

Vin - Vout (mV)

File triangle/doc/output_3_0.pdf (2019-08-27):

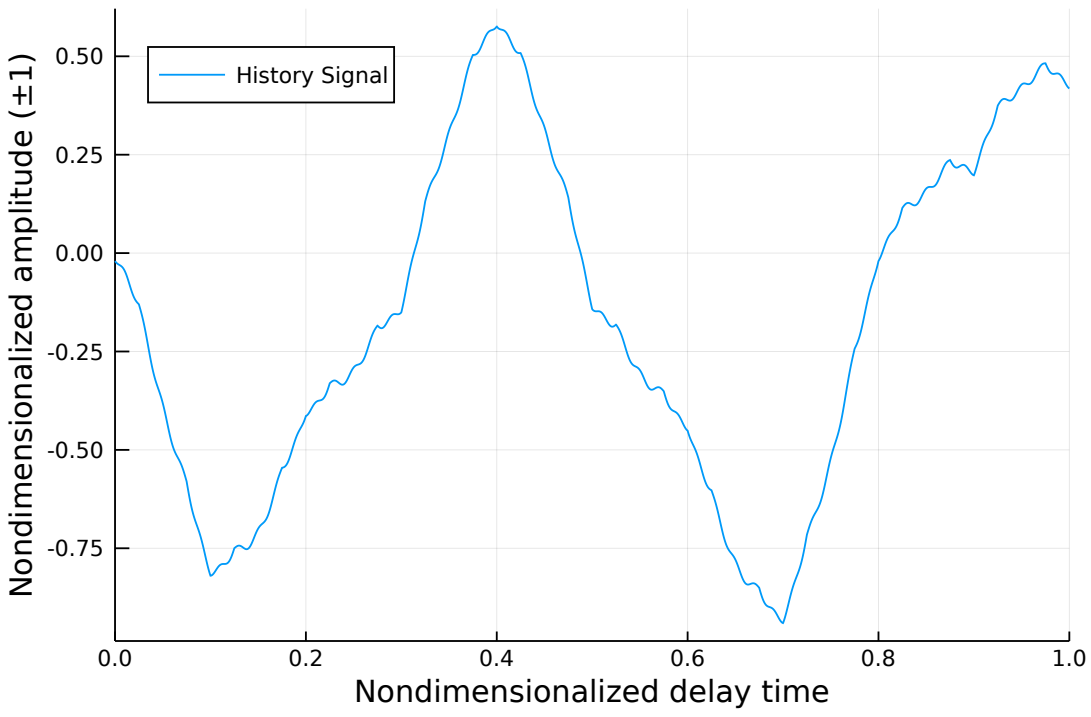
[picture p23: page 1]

Nondimensionalized amplitude (±1) History Signal

Nondimensionalized delay time

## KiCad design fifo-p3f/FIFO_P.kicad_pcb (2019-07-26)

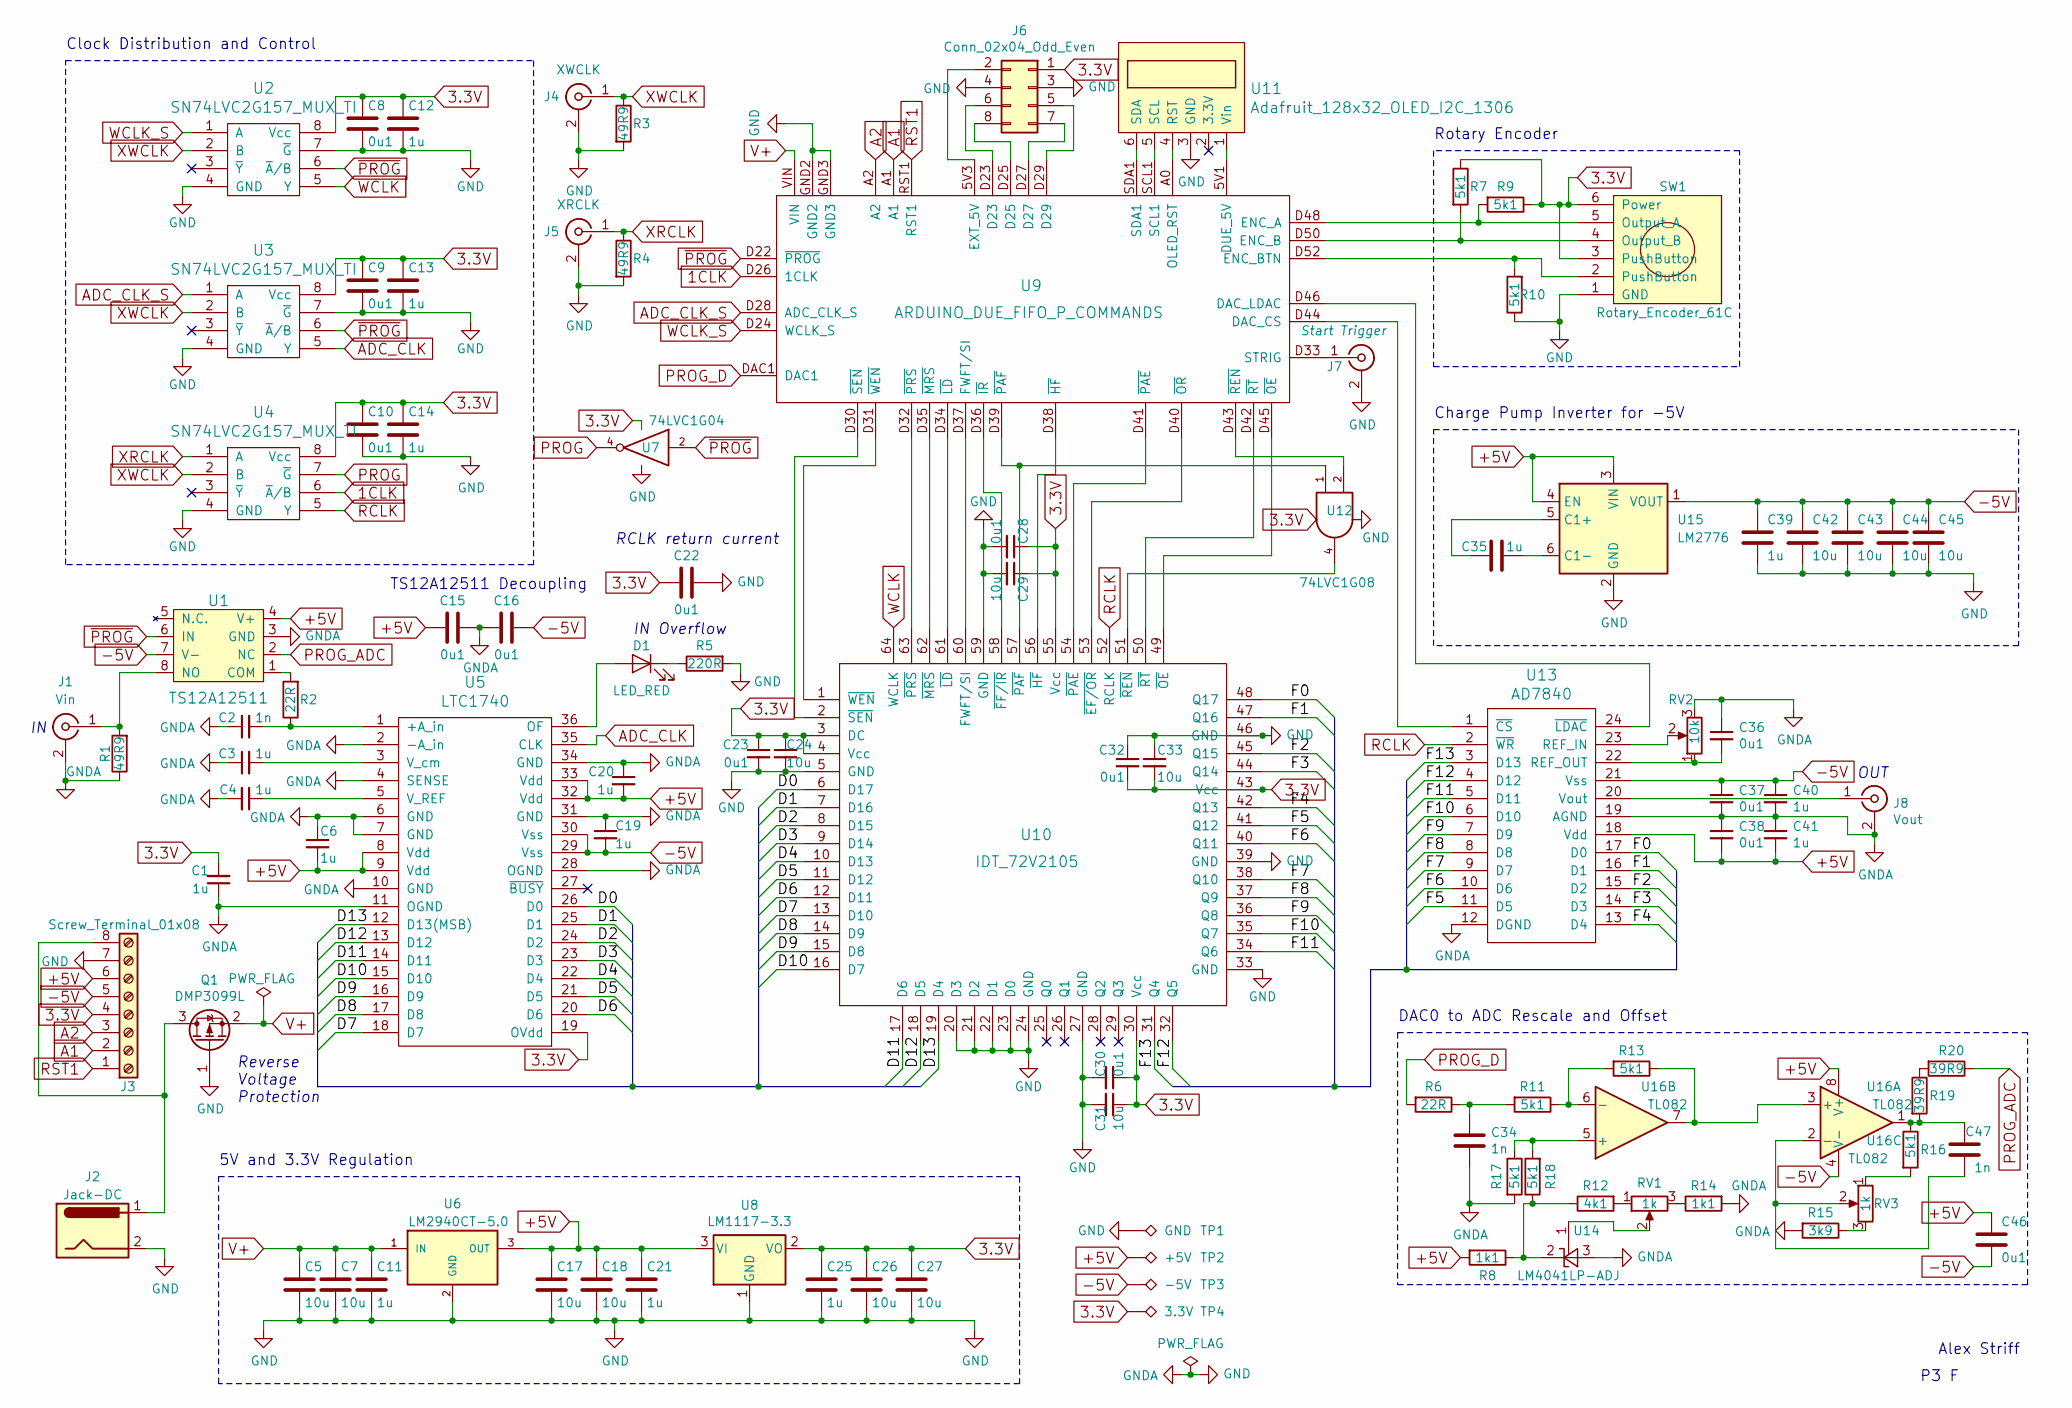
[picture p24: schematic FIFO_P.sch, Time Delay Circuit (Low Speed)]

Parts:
C1, C3, C4, C6, C11, C12, C13, C14, C19, C20, C21, C25, C35, C39, C40, C41: 1u; C_0805_2012Metric_Pad1.15x1.40mm_HandSolder
C2, C34, C47: 1n; C_0805_2012Metric_Pad1.15x1.40mm_HandSolder
C5, C7, C17, C18, C24, C26, C27, C29, C31, C33, C42, C43, C44, C45: 10u; C_0805_2012Metric_Pad1.15x1.40mm_HandSolder
C8, C9, C10, C15, C16, C22, C23, C28, C30, C32, C36, C37, C38, C46: 0u1; C_0805_2012Metric_Pad1.15x1.40mm_HandSolder
D1: LED_RED; LED_D3.0mm
J1: Vin; BNC_TEConnectivity_1478204_Vertical
J2: Jack-DC; BarrelJack_Horizontal
J3: Screw_Terminal_01x08; TerminalBlock_Phoenix_MKDS-3-8-5.08_1x08_P5.08mm_Horizontal
J4: XWCLK; BNC_TEConnectivity_1478204_Vertical
J5: XRCLK; BNC_TEConnectivity_1478204_Vertical
J6: Conn_02x04_Odd_Even; PinSocket_2x04_P1.27mm_Vertical
J7: Start Trigger; BNC_TEConnectivity_1478204_Vertical
J8: Vout; BNC_TEConnectivity_1478204_Vertical
Q1: DMP3099L; SOT-23
R1, R3, R4: 49R9; R_0805_2012Metric_Pad1.15x1.40mm_HandSolder
R2, R6: 22R; R_0805_2012Metric_Pad1.15x1.40mm_HandSolder
R5: 220R; R_0805_2012Metric_Pad1.15x1.40mm_HandSolder
R7, R9, R10, R11, R13, R16, R17, R18: 5k1; R_0805_2012Metric_Pad1.15x1.40mm_HandSolder
R8, R14: 1k1; R_0805_2012Metric_Pad1.15x1.40mm_HandSolder
R12: 4k1; R_0805_2012Metric_Pad1.15x1.40mm_HandSolder
R15: 3k9; R_0805_2012Metric_Pad1.15x1.40mm_HandSolder
R19, R20: 39R9; R_0805_2012Metric_Pad1.15x1.40mm_HandSolder
RV1, RV3: 1k; Potentiometer_Vishay_TS53YL_Vertical
RV2: 10k; Potentiometer_Bourns_3296W_Vertical
SW1: Rotary_Encoder_61C
TP1: GND; Test_Pin
TP2: +5V; Test_Pin
TP3: -5V; Test_Pin
TP4: 3.3V; Test_Pin
U1: TS12A12511; SOT-23-8_Handsoldering
U2, U3, U4: SN74LVC2G157_MUX_TI; SSOP-8_2.95x2.8mm_P0.65mm
U5: LTC1740; SSOP-36_5.3mm_Pitch0.65mm
U6: LM2940CT-5.0; TO-220-3_Horizontal_TabDown
U7: 74LVC1G04; SOT-23-5_HandSoldering
U8: LM1117-3.3; TO-252-3_TabPin2
U9: ARDUINO_DUE_FIFO_P_COMMANDS; Arduino_Due_Selected_Pins
U10: IDT_72V2105; LQFP-64_14x14mm_P0.8mm_HandSolder
U11: Adafruit_128x32_OLED_I2C_1306
U12: 74LVC1G08; SOT-23-5_HandSoldering
U13: AD7840; SSOP-24_5.3x8.2mm_P0.65mm
U14: LM4041LP-ADJ; SOT-23_Handsoldering
U15: LM2776; SOT-23-6
U16: TL082; SOIC-8_3.9x4.9mm_P1.27mm

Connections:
1CLK: U4.6 (~A~/B~), U9.D26 (1CLK)
3.3V: C1.2, C8.1, C9.1, C10.1, C12.1, C13.1, C14.1, C22.1, C23.1, C24.1, C25.1, C26.1, C27.1, C28.1, C29.1, C30.1, C31.1, C32.2, C33.2, J3.4, J6.1, R7.1, R9.1, SW1.3 (PushButton), SW1.6 (Power), TP4.1, U2.8 (Vcc), U3.8 (Vcc), U4.8 (Vcc), U5.19 (OVdd), U7.5 (VCC), U8.2 (VO), U10.3 (DC), U10.4 (Vcc), U10.30 (Vcc), U10.43 (Vcc), U10.55 (Vcc), U12.5 (VCC)
-5V: C16.2, C19.2, C37.1, C39.1, C40.1, C42.1, C43.1, C44.1, C45.1, C46.2, J3.5, TP3.1, U1.7 (V-), U5.29 (Vss), U5.30 (Vss), U13.21 (Vss), U15.1 (VOUT), U16.4 (V-)
/D0: U5.26 (D0), U10.6 (D17)
/D1: U5.25 (D1), U10.7 (D16)
/D2: U5.24 (D2), U10.8 (D15)
/D3: U5.23 (D3), U10.9 (D14)
/D4: U5.22 (D4), U10.10 (D13)
/D5: U5.21 (D5), U10.11 (D12)
/D6: U5.20 (D6), U10.12 (D11)
/D7: U5.18 (D7), U10.13 (D10)
/D8: U5.17 (D8), U10.14 (D9)
/D9: U5.16 (D9), U10.15 (D8)
/D10: U5.15 (D10), U10.16 (D7)
/D11: U5.14 (D11), U10.17 (D6)
/D12: U5.13 (D12), U10.18 (D5)
/D13: U5.12 (D13(MSB)), U10.19 (D4)
/F0: U10.48 (Q17), U13.17 (D0)
/F1: U10.47 (Q16), U13.16 (D1)
/F2: U10.45 (Q15), U13.15 (D2)
/F3: U10.44 (Q14), U13.14 (D3)
/F4: U10.42 (Q13), U13.13 (D4)
/F5: U10.41 (Q12), U13.11 (D5)
/F6: U10.40 (Q11), U13.10 (D6)
/F7: U10.38 (Q10), U13.9 (D7)
/F8: U10.37 (Q9), U13.8 (D8)
/F9: U10.36 (Q8), U13.7 (D9)
/F10: U10.35 (Q7), U13.6 (D10)
/F11: U10.34 (Q6), U13.5 (D11)
/F12: U10.32 (Q5), U13.4 (D12)
/F13: U10.31 (Q4), U13.3 (D13)
A1: J3.2, U9.A1
A2: J3.3, U9.A2
ADC_CLK: U3.5 (Y), U5.35 (CLK)
ADC_CLK_S: U3.1 (A), U9.D28 (ADC_CLK_S)
GND: C1.1, C2.1, C3.1, C4.2, C5.2, C6.1, C7.2, C8.2, C9.2, C10.2, C11.2, C12.2, C13.2, C14.2, C15.2, C16.1, C17.2, C18.2, C19.1, C20.1, C21.2, C22.2, C23.2, C24.2, C25.2, C26.2, C27.2, C28.2, C29.2, C30.2, C31.2, C32.1, C33.1, C34.2, C36.1, C37.2, C38.1, C39.2, C40.2, C41.1, C42.2, C43.2, C44.2, C45.2, J1.2 (Ext), J2.2, J3.7, J4.2 (Ext), J5.2 (Ext), J6.3, J6.4, J7.2 (Ext), J8.2 (Ext), Q1.1 (G), R1.1, R3.2, R4.2, R5.2, R10.1, R14.2, R15.2, R17.2, RV2.3, SW1.1 (GND), TP1.1, U1.3 (GND), U2.4 (GND), U2.7 (~G), U3.4 (GND), U3.7 (~G), U4.4 (GND), U5.2 (-A_in), U5.4 (SENSE), U5.6 (GND), U5.7 (GND), U5.10 (GND), U5.11 (OGND), U5.28 (OGND), U5.31 (GND), U5.34 (GND), U6.2 (GND), U7.3 (GND), U8.1 (GND), U9.GND2, U9.GND3, U10.5 (GND), U10.20 (D3), U10.21 (D2), U10.22 (D1), U10.23 (D0), U10.24 (GND), U10.27 (GND), U10.33 (GND), U10.39 (GND), U10.46 (GND), U10.59 (GND), U11.3 (GND), U12.3 (GND), U13.12 (DGND), U13.19 (AGND), U14.3 (A), U15.2 (GND)
unnamed: C2.2, R2.1, U5.1 (+A_in)
unnamed: C3.2, U5.3 (V_cm)
unnamed: C4.1, U5.5 (V_REF)
unnamed: C34.1, R6.1, R11.2
unnamed: C35.1, U15.6 (C1-)
unnamed: C35.2, U15.5 (C1+)
unnamed: C36.2, RV2.1, U13.22 (REF_OUT)
unnamed: D1.1 (K), R5.1
unnamed: D1.2 (A), U5.36 (OF)
unnamed: J1.1 (In), R1.2, U1.8 (NO)
unnamed: J2.1, J3.8, Q1.3 (D)
unnamed: J6.2, U9.5V3 (EXT_5V)
unnamed: J6.5, U9.D29
unnamed: J6.6, U9.D23
unnamed: J6.7, U9.D27
unnamed: J6.8, U9.D25
unnamed: J7.1 (In), U9.D33 (STRIG)
unnamed: J8.1 (In), U13.20 (Vout)
unnamed: R2.2, U1.1 (COM)
unnamed: R7.2, SW1.4 (Output_B), U9.D50 (ENC_B)
unnamed: R9.2, SW1.5 (Output_A), U9.D48 (ENC_A)
unnamed: R10.2, SW1.2 (PushButton), U9.D52 (ENC_BTN)
unnamed: R11.1, R13.2, U16.6 (-)
unnamed: R12.2, RV1.1
unnamed: R13.1, U16.3 (+), U16.7
unnamed: R14.1, RV1.3
unnamed: R15.1, RV3.3
unnamed: R16.2, RV3.1
unnamed: R19.1, R20.2
unnamed: RV1.2, U14.1 (FB)
unnamed: RV2.2, U13.23 (REF_IN)
unnamed: C47.2, RV3.2, U16.2 (-)
unnamed: U9.D31 (~WEN), U10.1 (~WEN)
unnamed: U9.D30 (~SEN), U10.2 (~SEN)
unnamed: U9.D45 (~OE), U10.49 (~OE)
unnamed: U9.D42 (~RT), U10.50 (~RT)
unnamed: U10.51 (~REN), U12.4
unnamed: U9.D40 (~OR), U10.53 (~EF/OR)
unnamed: U9.D41 (~PAE), U10.54 (~PAE)
unnamed: U9.D38 (~HF), U10.56 (~HF)
unnamed: U9.D39 (~PAF), U10.57 (~PAF), U12.1
unnamed: U9.D36 (~IR), U10.58 (~FF/IR)
unnamed: U9.D37 (FWFT/SI), U10.60 (FWFT/SI)
unnamed: U9.D34 (~LD), U10.61 (~LD)
unnamed: U9.D35 (~MRS), U10.62 (~MRS)
unnamed: U9.D32 (~PRS), U10.63 (~PRS)
unnamed: U9.5V1 (DUE_5V), U11.1 (Vin)
unnamed: U9.A0 (OLED_RST), U11.4 (RST)
unnamed: U9.SCL1, U11.5 (SCL)
unnamed: U9.SDA1, U11.6 (SDA)
unnamed: U9.D43 (~REN), U12.2
unnamed: U9.D44 (DAC_CS), U13.1 (~CS)
unnamed: U9.D46 (DAC_LDAC), U13.24 (~LDAC)
PROG: U4.7 (~G), U7.4
PROG_D: R6.2, U9.DAC1
RCLK: U4.5 (Y), U10.52 (RCLK), U13.2 (~WR)
RST1: J3.1, U9.RST1
V+: C5.1, C7.1, C11.1, Q1.2 (S), U6.1 (IN), U9.VIN
WCLK: U2.5 (Y), U10.64 (WCLK)
WCLK_S: U2.1 (A), U9.D24 (WCLK_S)
XRCLK: J5.1 (In), R4.1, U4.1 (A)
XWCLK: J4.1 (In), R3.1, U2.2 (B), U3.2 (B), U4.2 (B)
~PROG: U1.6 (IN), U2.6 (~A~/B~), U3.6 (~A~/B~), U7.2, U9.D22 (~PROG)

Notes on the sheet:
Rotary Encoder
P3 F
5V and 3.3V Regulation
Clock Distribution and Control
Charge Pump Inverter for -5V
DAC0 to ADC Rescale and Offset
TS12A12511 Decoupling
Reverse Voltage Protection
IN Overflow
OUT
RCLK return current
Alex Striff

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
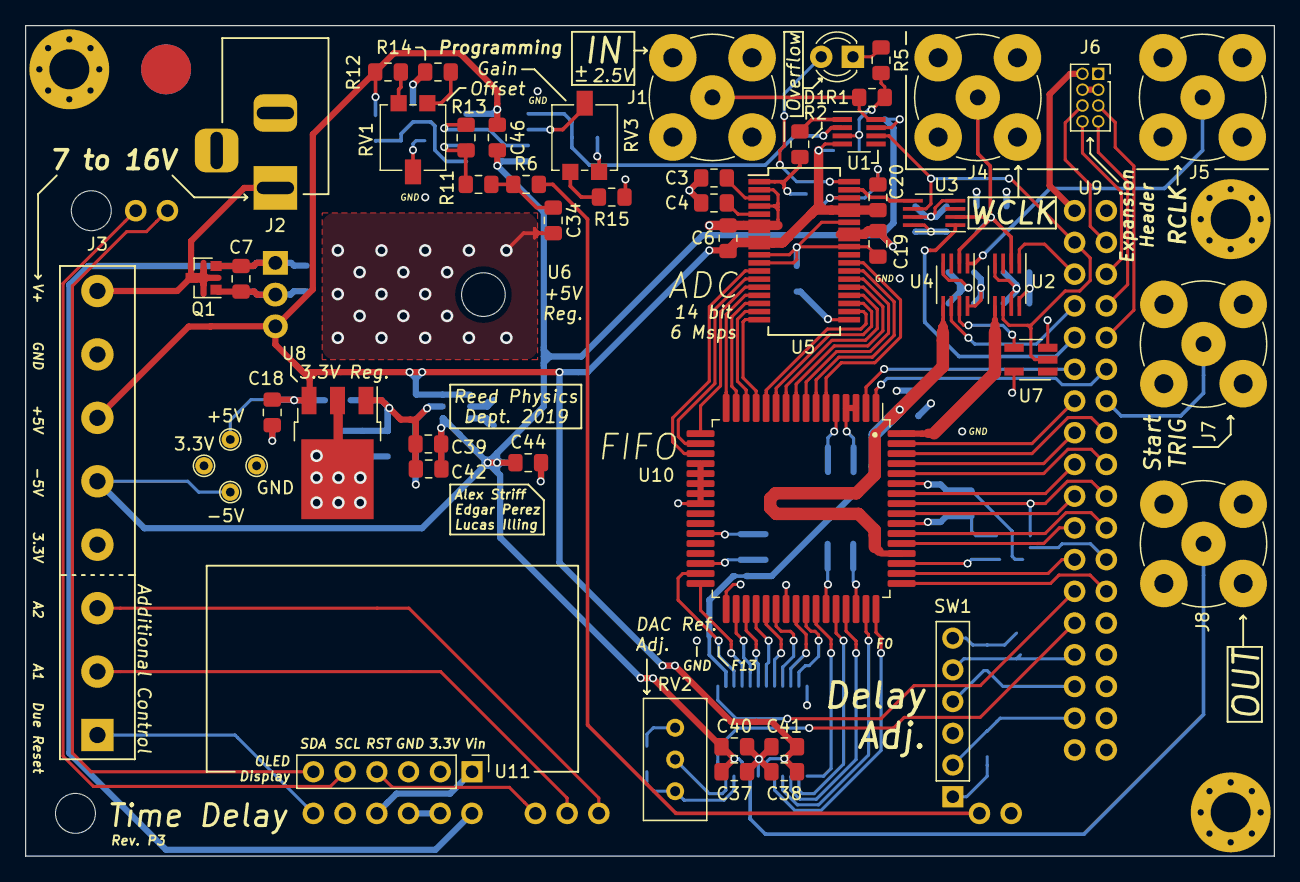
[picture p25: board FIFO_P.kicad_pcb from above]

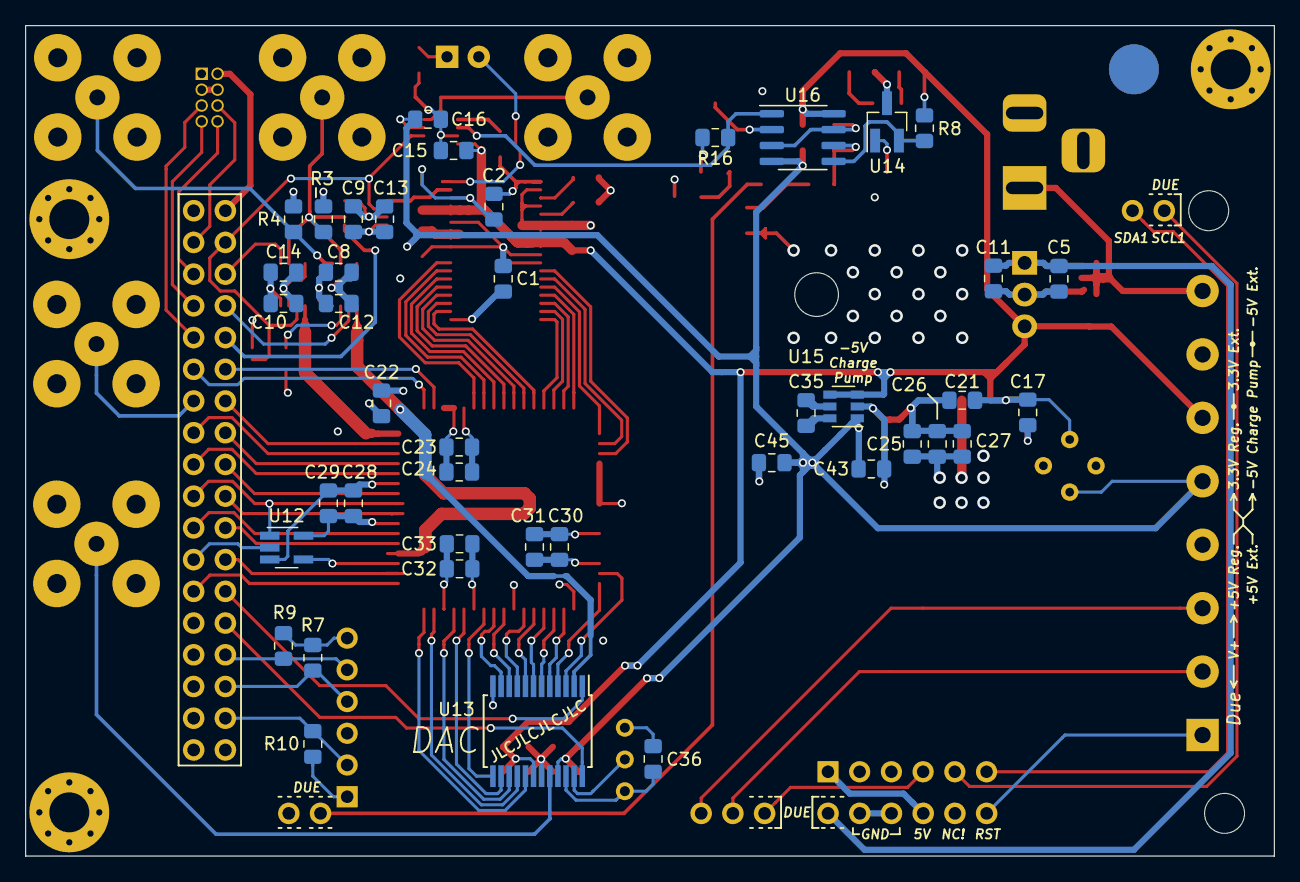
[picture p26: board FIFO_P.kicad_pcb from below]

Board: 4 copper layers, 100.0 x 66.5 mm, 96 parts (42 on the bottom side), 101 nets.

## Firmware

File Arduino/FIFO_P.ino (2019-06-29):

/*******************************************************************************
 * Time Delay Device Arduino Control
 * Edgar Perez and Alex Striff
 * Reed College Physics Department
 *
 * For more information, contact Lucas Illing <illing@reed.edu>.
 *
 * Version  Date        Author       Changes
 * -------  ----------  -----------  -----------------------------------------------
 * v1.0.0   2016-12-15  Edgar Perez  Prototype completed.
 * v1.0.1   2019-06-XX  Alex Striff  Modified for publication board.
 *
 * Notes
 * =====
 * By pressing down the rotary encoder's push button, the encoder takes steps
 * of 1000 words instead of a single word (set by the `count_mul` variable).
 *
 ********************************************************************************/

// Uncomment to enable LCD output.
// #define LCD

#ifdef LCD
#include <Wire.h>
#include <Adafruit_RGBLCDShield.h>
#include <utility/Adafruit_MCP23017.h>

#define RED     0x1 << 0
#define GREEN   0x1 << 1
#define BLUE    0x1 << 2
#define YELLOW  RED   | GREEN
#define TEAL    GREEN | BLUE
#define VIOLET  RED   | BLUE
#define WHITE   RED   | GREEN | BLUE

// The LCD uses the I2C SCL and SDA pins.
Adafruit_RGBLCDShield lcd = Adafruit_RGBLCDShield();
char toprow[16];
int cursloc;
#endif // LCD

typedef const uint8_t pin;

typedef struct {
    pin p;                      // The pin that the button is connected to.
    long debounce_delay;        // The delay for debouncing a button press.
    int state;                  // The current state of the button.
    int last_state;             // The last state of the button.
    long last_debounce_time;    // The last debounce time for the button.
} button;

typedef struct {
    pin a;          // Output A
    pin b;          // Output B
    button btn;     // Button (knob of encoder)
} rotary_encoder;

// FIFO word limits
const uint32_t min_words = 3;
const uint32_t max_words = 262144;

// Rotary encoder pin mapping
rotary_encoder enc = {
    .a   = 25,
    .b   = 26,
    .btn = {
        .p = 28,
        .debounce_delay = 10,
        .state = 0,
        .last_state = 0,
        .last_debounce_time = 0
    }
};

uint32_t words   = 10; // This variable will be changed by (initial) encoder input
int32_t  count_min = min_words;
int32_t  count_max = max_words;
int32_t  count_mul = 1000;

// Clock enabling (for DAC setup)
pin CLK_EN = 7;

// FIFO pin mapping
pin OE     = 22;
pin RT     = 23;
pin REN    = 24;
pin OR     = 27;
pin PAE    = 29;
pin HF     = 34;
pin PAF    = 37;
pin IR     = 38;
pin FWFTSI = 39;
pin LD     = 40;
pin MRS    = 41;
pin PRS    = 42;
pin WCLK   = 46;
pin WEN    = 45;
pin SEN    = 44;
pin WLSTN  = 47;

// ADC pin mapping
pin DAC_LDAC = 3;
pin DAC_CS   = 4;

// FIFO constant mapping
int PAF_flag;

// Serial buffers
#define SBLEN   8
#define SBBLEN  9
char sb[SBLEN];
char sbb[SBBLEN];


void setup(void)
{
    // Serial communication
    Serial.begin(115200);
    Serial.println("===================");
    Serial.println(" Time Delay Device ");
    Serial.println("===================");
    Serial.println("Type 'h' for help.");
    Serial.print("Setting up I/O ... ");

    // FIFO pins
    pinMode(OE, OUTPUT);
    pinMode(RT, OUTPUT);
    pinMode(REN, INPUT);
    pinMode(OR, INPUT_PULLUP);
    pinMode(PAE, INPUT_PULLUP);
    pinMode(HF, INPUT_PULLUP);
    pinMode(PAF, INPUT_PULLUP);
    pinMode(IR, INPUT_PULLUP);
    pinMode(FWFTSI, OUTPUT);
    pinMode(LD, OUTPUT);
    pinMode(MRS, OUTPUT);
    pinMode(PRS, OUTPUT);
    pinMode(WCLK, OUTPUT);
    pinMode(WEN, OUTPUT);
    pinMode(SEN, OUTPUT);
    pinMode(WLSTN, OUTPUT);

    // FIFO default states
    digitalWrite(MRS, HIGH);
    digitalWrite(PRS, HIGH);
    digitalWrite(RT, HIGH);
    digitalWrite(FWFTSI, HIGH);
    digitalWrite(LD, HIGH);
    digitalWrite(WEN, HIGH);
    digitalWrite(REN, HIGH);
    digitalWrite(SEN, HIGH);
    digitalWrite(OE, LOW);
    digitalWrite(WCLK, LOW);
    digitalWrite(WLSTN, LOW);

    // DAC pins and boot
    pinMode(DAC_CS, OUTPUT);
    pinMode(CLK_EN, OUTPUT);
    pinMode(DAC_LDAC, OUTPUT);
    digitalWrite(CLK_EN, LOW);
    digitalWrite(DAC_LDAC,HIGH);
    delay(5);
    digitalWrite(CLK_EN,HIGH);
    digitalWrite(DAC_LDAC,LOW);

    digitalWrite(DAC_CS, HIGH);
    delay(5);
    digitalWrite(DAC_CS, LOW);
    delay(5);
    digitalWrite(DAC_CS, HIGH);
    delay(5);
    digitalWrite(DAC_CS, LOW);

    // Rotary encoder
    pinMode(enc.btn.p, INPUT_PULLUP);
    pinMode(enc.a, INPUT_PULLUP);
    digitalWrite(enc.a, HIGH);
    pinMode(enc.b, INPUT_PULLUP);
    digitalWrite(enc.b, HIGH);

    #ifdef LCD
    // LCD
    lcd.begin(16, 2);
    lcd.setBacklight(WHITE);
    lcd.print("Hello, world!2");
    #endif // LCD

    // Do a master reset to initialize the FIFO
    Serial.print(" complete. Initializing FIFO:\n\t");
    delay(5);
    master_reset();
    Serial.println();
}


void loop(void)
{
    unsigned long narg;

    live_rotor();

    if (Serial.available() > 0) {
        Serial.readBytesUntil('*', sbb, SBBLEN);
        for (int i = 1; i < SBBLEN; i++) {
            sb[i-1] = sbb[i];
        }

        narg = atol(sb);
        switch (sbb[0]) {
            case 'h': // Fallthrough.
            case 'H': // Fallthrough.
            case '?': serial_help(); break;
            case 'm':
                if(sb[0] == 'r')
                    master_reset();
                else
                    unknown();
                break;
            case 'p':
                if(sb[0] == 'r')
                    partial_reset();
                else
                    unknown();
                break;
            case 'd': set_delay(narg); break;
            case 's': report_status(); break;
            case 'x': pause(narg); break;
            case 'i': initialize(); break;
            case 'q': quit(); break;
            default:
                unknown();
                
        }

        sbbclear();
    }
}


void unknown(void)
{
    Serial.println("Unknown Command. Type 'h' for help.");
    serial_help();
}


void serial_help(void)
{
    Serial.print(
            "Time Delay Device Serial Commands\n"
            "=================================\n"
            "mr\tPerforms a master reset of FIFO memory.\n"
            "pr\tPerforms a partial reset of FIFO memory.\n"
            "d N\tSets delay to N words, where N is a decimal number between ");
    Serial.print(min_words, DEC);
    Serial.print(" and ");
    Serial.print(max_words, DEC);
    Serial.print(
            ".\n"
            "\tE.g.: 'D3' and 'D100' produce delays of 3 and 100 words, respectively.\n"
            "\tValues outside this range will be clamped, so 'D0' is the same as 'D3'.\n"
            "\t<time delay> = <delay words> * <clock period>.\n"
            "s\tReports FIFO status.\n"
            "x N\tPauses for N seconds.\n"
            "i\tInitializes the program.\n"
            "q\tQuits the program.\n"
            "h H ?\tShows this help.\n"
            "\n"
            );
}


void sbshift(void)
{
    sb[0] -= 48;
    for (int i = SBLEN - 1; i > 0; i--)
        sb[i] = sb[i-1];
}


void sbclear(void)
{
    for(int i = 0; i < SBLEN; i++)
        sb[i] = 0;
}


void sbbclear(void)
{
    for(int i = 0; i < SBBLEN; i++)
        sbb[i] = 0;
}


void partial_reset(void)
{
    long t1, t2;
    Serial.print("Partial Reset ... ");
    t1 = micros();
    digitalWrite(WLSTN, 1);
    delay(1);
    digitalWrite(REN, 1);
    digitalWrite(WEN, 1);
    digitalWrite(RT, 1);
    delayMicroseconds(3);
    digitalWrite(PRS,LOW);
    delayMicroseconds(3);
    digitalWrite(PRS,HIGH);
    delayMicroseconds(3);
    digitalWrite(WEN, 0);
    digitalWrite(WLSTN, 0);
    t2 = micros() - t1;
    Serial.print("done (");
    Serial.print(t2);
    Serial.print(" us).\n");
}


void master_reset(void)
{
    long t1, t2;
    Serial.print("Master Reset ... ");
    t1 = micros();
    digitalWrite(FWFTSI, HIGH);
    digitalWrite(LD, HIGH);
    digitalWrite(MRS, LOW);
    delayMicroseconds(1);
    digitalWrite(MRS,HIGH);
    t2 = micros() - t1;
    delayMicroseconds(1);
    Serial.print("done (");
    Serial.print(t2);
    Serial.println(" us).");
    Serial.print("Device in FWFT with Serial Loading.\n");
}


void report_status(void)
{
    Serial.println("FIFO Status");
    Serial.println("===========");
    Serial.print("IR\t"); Serial.println(digitalRead(IR));
    Serial.print("OR\t"); Serial.println(digitalRead(OR));
    Serial.print("PAF\t"); Serial.println(digitalRead(PAF));
    Serial.print("PAE\t"); Serial.println(digitalRead(PAE));
    Serial.print("HF\t"); Serial.println(digitalRead(HF));
    Serial.println();
}


void pause(unsigned int n)
{
    for(int i = 0; i < n; i++) {
        Serial.println(n - i);
        delay(1000);
    }
    Serial.println(0);
}


void set_delay(unsigned int n)
{
    unsigned int m;
    int bits;
    
    n = clamp(n, min_words, max_words);
    words = n;
    m = max_words - n;
    
    Serial.print("Sending a "); Serial.print(n); Serial.print(" word delay ... ");
    digitalWrite(WLSTN, 1);
    delayMicroseconds(10);

    digitalWrite(WCLK, 0);
    digitalWrite(LD, 0);
    digitalWrite(SEN, 0);
    delayMicroseconds(2);

    // The following number is defined because PAF triggers at the given
    // number of words AWAY FROM the end, not AT the given word like PAE.
    for (int i = 0; i < 36 ; i++) {
        bits = i == 0 ? 1 : bitRead(m, i - 18);
        digitalWrite(FWFTSI, bits);
        delayMicroseconds(1);
        digitalWrite(WCLK, 1);
        delayMicroseconds(1);
        digitalWrite(WCLK, 0);
    }

    digitalWrite(LD, 1);
    digitalWrite(SEN, 1);
    digitalWrite(WLSTN, 0);
    Serial.print("done. Resetting: ");
    partial_reset();

    #ifdef LCD
    sprintf(toprow, "D.Words = %06u", n);
    lcd.home();
    lcd.clear();
    lcd.print(toprow);
    #endif // LCD
}


void initialize(void)
{
    digitalWrite(WEN, 0);
    digitalWrite(REN, 0);
    Serial.println("Initiated program.");
}


void quit(void)
{
    digitalWrite(WEN, 1);
    digitalWrite(REN, 1);
    Serial.println("Quit program.");
}


int8_t read_encoder(rotary_encoder *e)
{
    static int8_t enc_states[4][4] = {
        { 0, -1,  1,  0},
        { 1,  0,  0, -1},
        {-1,  0,  0,  1},
        { 0,  1, -1,  0}
    };
    static uint8_t old_AB = 0;
    int8_t direction;
    uint8_t AB = digitalRead(e->a) << 1 | digitalRead(e->b);

    direction = enc_states[old_AB][AB];
    old_AB = AB;

    return direction;
}


int32_t clamp(int32_t x, int32_t min, int32_t max)
{
    return x <= min ? count_min : x >= max ? max : x;
}


uint32_t rotary(void)
{
    int8_t  tmpdata;
    int32_t mul;
    int32_t count = words;
    tmpdata = read_encoder(&enc);

    if (tmpdata) {
        mul = read_button(&(enc.btn)) ? count_mul : 1;
        count += mul * tmpdata;
        count = clamp(count, count_min, count_max);
    }

    return (uint32_t) count;
}


void live_rotor(void)
{
    uint32_t rotorvalc = rotary();
    
    if (rotorvalc != words) {
        set_delay(rotorvalc);
    }
}


int read_button(button *button)
{
    int reading = digitalRead(button->p);
    if (reading != button->last_state){
        button->last_debounce_time = millis();
    }

    if (millis() - button->last_debounce_time > button->debounce_delay) {
        if (reading != button->state) {
            button->state = reading;
        }
        return button->state;
    } else {
        button->last_state = reading;
    }
}

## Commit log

2019-06-18 Initial upload
    Contains working files with no external dependencies. Rev 3 not included
    [528A.DSN, 528A.xls, Expenses.xlsx, FIFO_P-B.Cu.gbr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]
2019-06-19 Fixed footprints; deleted PCB.
    [528A.DSN, 528A.xls, Expenses.xlsx, FIFO_P-B.Cu.gbr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]
2019-06-19 Created 4-layer PCB
    [FIFO_P.kicad_pcb]
2019-06-19 Fix arduino header, started laying out connectors
    The pins used were changed, so the old code must be rewritten to use the new pins and port D instead of port A.
    [FIFO_P.kicad_pcb, FIFO_P.sch, FIFO_P_power.sch]
2019-06-20 ADC to FIFO routing
    [FIFO_P.kicad_pcb, FIFO_P.sch]
2019-06-22 Most routing done
    [FIFO_P.kicad_pcb, FIFO_P.sch, FIFO_P_power.sch]
2019-06-24 Added inverter for -5V
    [FIFO_P.kicad_pcb, FIFO_P.sch, FIFO_P_power.sch]
2019-06-24 Partial jumpers
    [FIFO_P.kicad_pcb, FIFO_P.sch, FIFO_P_power.sch]
2019-06-25 Cleanup; prepared to route header
    [FIFO_P.kicad_pcb]
2019-06-25 Routed FIFO-DAC header
    [FIFO_P.kicad_pcb]
2019-06-25 Moved power
    [FIFO_P.kicad_pcb, FIFO_P.sch]
2019-06-26 Actually fixed power and clocks
    TODO: Flip arduino header and reroute
    [FIFO_P.kicad_pcb]
2019-06-26 Fixed Arduino mounting holes
    [FIFO_P.kicad_pcb]
2019-06-26 Started silkscreen
    [FIFO_P.kicad_pcb]
2019-06-26 Cleaned up old files
    [2017 Expenses.xlsx, FIFO_P-B.Cu.gbr, FIFO_P-B.Mask.gbr, FIFO_P-Cmts.User.gbr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]
2019-06-26 Silkscreen cleaned up on both sides
    [FIFO_P-B_Cu.gbr, FIFO_P-B_Mask.gbr, FIFO_P-B_Paste.gbr, FIFO_P-B_SilkS.gbr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]
2019-06-26 More tweaks
    [FIFO_P.kicad_pcb]
2019-06-27 Added screw terminal footprint
    [FIFO_P.kicad_pcb]
2019-06-27 Fixed RV refdes
    [FIFO_P.kicad_pcb]
2019-06-27 Fixed RCLK trace
    [FIFO_P.kicad_pcb]
2019-06-27 Fix ferrite soldermask
    [FIFO_P.kicad_pcb]
2019-06-27 Fixed FIFO pin
    [FIFO_P.kicad_pcb, FIFO_P.sch]
2019-06-27 Cleaned up input limit silkscreen
    [FIFO_P.kicad_pcb]
2019-06-27 Add ADC specs
    [FIFO_P.kicad_pcb]
2019-06-28 Swapped RT and OE to be sensible
    [FIFO_P.kicad_pcb]
2019-06-29 Add original Arduino code
2019-06-29 Cleaned up Arduino code
2019-06-29 Renamed Arduino code to FIFO_P
2019-07-01 Routed SMT DAC
    Modified from after Edgar's changes
    [2017 Expenses.xlsx, FIFO_P.kicad_pcb]
2019-07-02 Add _partial_ BOM, minor tweaks to PCB
    [FIFO_P.csv, FIFO_P.kicad_pcb]
2019-07-02 Final revision before manufacture
    [FIFO_P.kicad_pcb]
2019-07-03 Added Gerbers and locked Due on pcb
    [FIFO_P-B_Cu.gbr, FIFO_P-B_Mask.gbr, FIFO_P-B_SilkS.gbr, FIFO_P-Cmts_User.gbr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]
2019-07-16 Begin cleaning up schematic. FIFO-DAC area ripped up
    [FIFO_P.kicad_pcb, FIFO_P.sch, FIFO_P_power.sch]
2019-07-16 Updated missing footprints on schematic
    [FIFO_P.sch]
2019-07-16 More schematic cleanup: reannotate and re-do footprints
    [FIFO_P.sch]
2019-07-16 Added screw terminal; put some new IC footprints in place
    [FIFO_P.kicad_pcb, FIFO_P.sch, FIFO_P_power.sch]
2019-07-16 Flipped Due pins to be correct to actual
    [FIFO_P.kicad_pcb, FIFO_P.sch, FIFO_P_power.sch]
2019-07-17 More progress on final board
    [FIFO_P.kicad_pcb, FIFO_P.sch, FIFO_P_power.sch]
2019-07-17 Reannotated and replaced many components. Bypass capacitors everywhere.
    [FIFO_P.kicad_pcb, FIFO_P.sch, FIFO_P_power.sch]
2019-07-17 Remapped some Due pins; fixed FIFO output vias
    [FIFO_P.kicad_pcb]
2019-07-18 More work, idk what I even changed at this point... lots of stuff
    [FIFO_P.kicad_pcb]
2019-07-19 More work. TODO: Change muxes to clock ADC and both R/WCLKs, not RCLK and WCLK
    [FIFO_P.kicad_pcb, FIFO_P.sch]
2019-07-20 Finished DAC0 to ADC rescale circuit; rerouted power
    [FIFO_P.kicad_pcb, FIFO_P.sch]
2019-07-22 Calculated optimum DAC0 to ADC resistor values and fixed schematic
    [FIFO_P.sch]
2019-07-23 Updated schematic for dual clock operation; Squished everything!
    [FIFO_P.kicad_pcb, FIFO_P.sch]
2019-07-23 Fixed Due power and added AND gate for FIFO ~RE
    [FIFO_P.kicad_pcb, FIFO_P.sch]
2019-07-24 Almost done routing!
    [FIFO_P.kicad_pcb, FIFO_P.sch]
2019-07-24 Done with main circuit. TODO: EXT header and input protection
    [FIFO_P.kicad_pcb, FIFO_P.sch]
2019-07-25 Board pretty much done. Cleaned up silkscreen
    [FIFO_P.kicad_pcb, FIFO_P.sch]
2019-07-25 Fixed 1CLK signal. Board complete.
    [FIFO_P.kicad_pcb, FIFO_P.sch]
2019-07-25 Fixed power in voltage and specified layer stackup
    [FIFO_P.kicad_pcb]
2019-07-25 Moved power connector for new Due header clearance
    [FIFO_P.csv, FIFO_P.kicad_pcb, FIFO_P.sch]
2019-07-25 Made expansion header smaller
    [FIFO_P.kicad_pcb, FIFO_P.sch]
2019-07-26 Final order PCB. Added Gerbers
    [FIFO_P-B_Cu.gbr, FIFO_P-B_Mask.gbr, FIFO_P-B_SilkS.gbr, FIFO_P-Cmts_User.gbr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]
2019-07-26 Updated schematic PDF and Arduino pin mappings
2019-07-28 Add GLAD module schematic
    [glad.kicad_pcb, glad.sch]
2019-07-30 Fix RV2 to be a bit more friendly to the DAC reference
    [FIFO_P.sch]
2019-08-01 GLAD schematic PDF; Fixed RV2 to be a bit more friendly to the DAC reference
    [FIFO_P.sch]
2019-08-07 Circuit fixes and debugging; Everything provisionally works
    [FIFO_P.sch]
2019-08-10 Add characterization work so far
    [Tek000.csv, Tek001.csv, Tek002.csv, Tek003.csv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]
2019-08-12 Applying different filters to 5 MHz difference data
2019-08-15 Output filter data and difference plots
2019-08-20 Dumped data to plot
    [test.csv]
2019-08-21 Publication figures with gnuplot
    [delay_linearity_remainder.csv, delayplot.csv, test.csv]
2019-08-27 Moved KiCAD files to a subdirectory
    [FIFO_P-B_Cu.gbr, FIFO_P-B_Mask.gbr, FIFO_P-B_Paste.gbr, FIFO_P-B_SilkS.gbr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]
2019-08-27 Renamed directories
    [528A.DSN, 528A.xls, FIFO_P-B_Cu.gbr, FIFO_P-B_Mask.gbr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]
2019-08-27 Added documentation
    [528A.DSN, 528A.xls, delay_linearity.csv, delay_linearity.xlsx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]
